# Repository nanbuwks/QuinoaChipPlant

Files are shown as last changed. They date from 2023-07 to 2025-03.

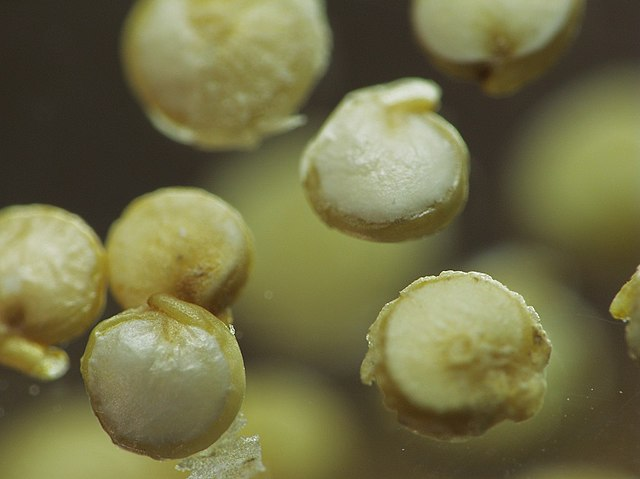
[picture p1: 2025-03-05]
images/2023-03-23-17-26-28.png

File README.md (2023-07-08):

# QuinoaChipPlant

キヌアの育種のために、撒種→結実を速いサイクルで回すためのプラントです。

## キヌアとは

キヌア（ Quinua ):南米で食されている雑穀。
栄養的に優れていて、スーパーフードとして注目されている。
乾燥/湿地、低温、塩地などの他の作物が育たない環境でも栽培ができる。
遺伝子が多様で、品種改良が期待される。

## このプラントの目的

1つのチップに1粒ずつ撒種し、水耕栽培を行います。
1つのラックにチップが24収納できますが、チップ1つ分はセンサーのために使うので1つのラックで23粒を撒きます。
芽が出たら1つのラックに10程度に間引きします。
100ラックで実験するとなると、1000株を育成することになります。
収量を目的とするのではなく、促成で種を回収することを目的としています。

# 育成ロボット

水換え、光照射、センサ接続ができるロボットボードです。
1000株分を育成するのは水替えも大変なので、自動で水換えを行います。
プログラムで自動運転できるので、一時冠水を繰り返すような運転を行うことができます。

## 組み立て方、使い方

「キヌア栽培のための制御回路をつくってみよう」
https://qiita.com/nanbuwks/items/138a8bbda59f0657b9df

## 開発コミュニティ

discord OpenHardTerrace 中の #chipplant で開発しています。
https://discord.gg/T8mKzFyu6m

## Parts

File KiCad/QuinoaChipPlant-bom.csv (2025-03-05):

ID | 指定子 | フットプリント | 数量 | 名称 | 供給業者、参考資料
1 | U2,U8,U6,U3,U4 | SparkFun_TB6612FNG_MOTOR_DRIVER_MODULE | 5 | SparkFun_TB6612FNG_MOTOR_DRIVER_MODULE
2 | J11 | JST_XH_B4B-XH-AM_1x04_P2.50mm_Vertical | 1 | LEVEL2
3 | J7,J10,J16,J9,J15,J8 | JST_XH_B2B-XH-AM_1x02_P2.50mm_Vertical | 6 | BULB
4 | D1,D4,D18,D3,D5,D7,D2,D11,D6,D10 | D_SOD-123 | 10 | D
5 | R10,R8,R9,R7 | R_1206_3216Metric_Pad1.30x1.75mm_HandSolder | 4 | 10K
6 | R16,R6,R15,R13,R14,R3,R17,R4,R12,R11,R5,R19,R20,R18 | R_1206_3216Metric_Pad1.30x1.75mm_HandSolder | 14 | 470
7 | ,,,,,,, |  | 8
8 | U5 | Seeedstudio_Grove_110990030_Vertical_4pin_2mmpitch | 1 | SEEED_GROVE
9 | J6,J5 | JST_XH_B2B-XH-AM_1x02_P2.50mm_Vertical | 2 | MOTOR
10 | D8,D9,D16,D15,D17,D14,D20,D13,D19,D12 | LED_D3.0mm | 10 | LED
11 | J4,J20 | TerminalBlock_Phoenix_PT-1,5-4-5.0-H_1x04_P5.00mm_Horizontal | 2 | Screw_Terminal_01x04
12 | U9 | YRB_YMD-10WR3_YRA_YMD-10WR3 | 1 | ~
13 | C5 | C_1206_3216Metric_Pad1.33x1.80mm_HandSolder | 1 | 0.1uF
14 | BZ1 | Buzzer_12x9.5RM7.6 | 1 | Buzzer
15 | C7,C9,C8,C14,C6,C16,C17,C10,C11,C12,C13 | R_1206_3216Metric_Pad1.30x1.75mm_HandSolder | 11 | C
16 | C3,C1 | C_1206_3216Metric_Pad1.33x1.80mm_HandSolder | 2 | C
17 | J13 | JST_XH_B4B-XH-AM_1x04_P2.50mm_Vertical | 1 | LEVEL4
18 | U1 | ESP32_DEVKIT_V1 | 1 | ESP32_DEVKIT_V1
19 | J3 | JST_XH_B4B-XH-AM_1x04_P2.50mm_Vertical | 1 | LEVEL1
20 | C2,C4,C15 | CP_Radial_D10.0mm_P2.50mm_P5.00mm | 3 | C_Polarized
21 | J18,J1 | JST_PH_B4B-PH-K_1x04_P2.00mm_Vertical | 2 | GROVE
22 | J2 | DCJACK | 1 | DCJACK
23 | TH1 | TerminalBlock_Phoenix_MKDS-1,5-2_1x02_P5.00mm_Horizontal | 1 | Thermistor
24 | J14 | DCJACK | 1 | DCJACK OPTIONAL
25 | U7 | TFT3.2_ILI9341 | 1 | CR2013-MI2120
26 | SW1 | SW_PUSH_6mm | 1 | SW_Push
27 | J12 | JST_XH_B4B-XH-AM_1x04_P2.50mm_Vertical | 1 | LEVEL3
28 | R1 | R_1206_3216Metric_Pad1.30x1.75mm_HandSolder | 1 | R
29 | JP3 | SolderJumper-2_P1.3mm_Bridged_Pad1.0x1.5mm | 1 | SolderJumper_2_Bridged

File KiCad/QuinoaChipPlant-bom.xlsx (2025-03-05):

Comment | Designator | Footprint | JLCPCB Part #（optional）
SparkFun_TB6612FNG_MOTOR_DRIVER_MODULE | U2,U8,U6,U3,U4,U12,U18,U16,U13,U14 | SparkFun_TB6612FNG_MOTOR_DRIVER_MODULE | C718237
LEVEL2 | J11 | LEVEL2 | C144395
BULB | J7,J10,J16,J9,J15,J8 | BULB | C158012
D | D1,D4,D18,D3,D5,D7,D2,D11,D6,D10 | D | C397619
10K | R10,R8,R9,R7 | 10K | C17902
470 | R16,R6,R15,R13,R14,R3,R17,R4,R12,R11,R5,R19,R20,R18 | 470 | C17936
SEEED_GROVE | U5 | SEEED_GROVE | C146064
MOTOR | J6,J5 | MOTOR | C158012
LED | D8,D9,D16,D15,D17,D14,D20,D13,D19,D12 | LED | C779429
Screw_Terminal_01x04 | J104,J120,J114,J130 | Screw_Terminal_01x02x02 | C8404
0.1uF | C5 | 0.1uF | C24497
Buzzer | BZ1 | Buzzer | C96222
C | C7,C9,C8,C14,C6,C16,C17,C10,C11,C12,C13 | C | C24497
C | C3,C1 | C | C24497
LEVEL4 | J13 | LEVEL4 | C144395
ESP32_DEVKIT_V1 | U1,U11 | ESP32_DEVKIT_V1 | C2897378
LEVEL1 | J3 | LEVEL1 | C144395
DCJACK | J2 | DCJACK | C16214
Thermistor | TH1 | Thermistor | C8404
CR2013-MI2120 | U7 | CR2013-MI2120 | C2897377
SW_Push | SW1 | SW_Push | C455098
LEVEL3 | J12 | LEVEL3 | C144395
R | R1 | R | C17902

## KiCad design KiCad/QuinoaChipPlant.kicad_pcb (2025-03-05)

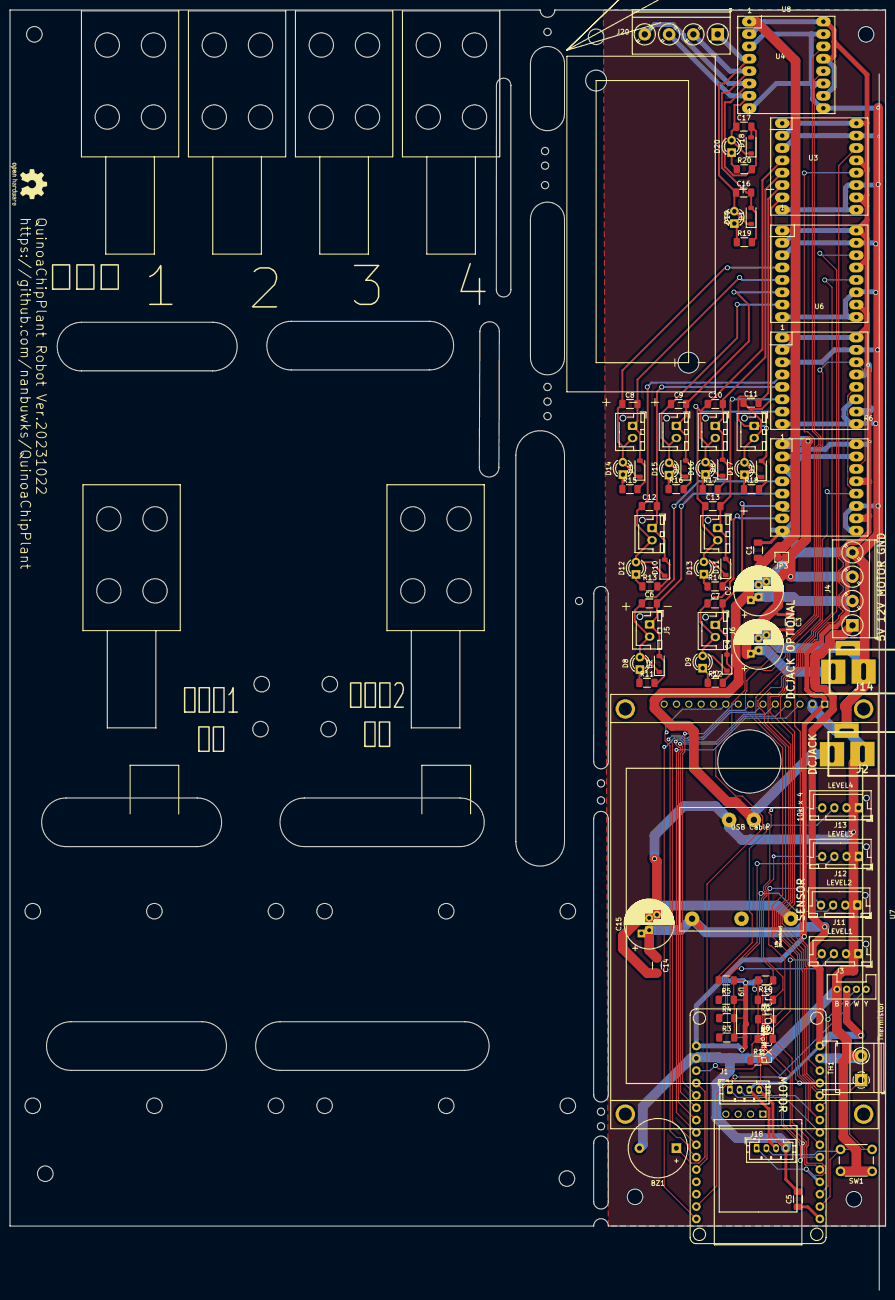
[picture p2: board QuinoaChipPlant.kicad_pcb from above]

Board: 2 copper layers, 180.0 x 263.2 mm, 138 parts (0 on the bottom side), 63 nets.

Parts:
BZ1: Buzzer; Buzzer_12x9.5RM7.6
C1, C3: C; C_1206_3216Metric_Pad1.33x1.80mm_HandSolder
C2, C4, C15: C_Polarized; CP_Radial_D10.0mm_P2.50mm_P5.00mm
C5: 0.1uF; C_1206_3216Metric_Pad1.33x1.80mm_HandSolder
C6, C7, C8, C9, C10, C11, C12, C13, C14, C16, C17: C; R_1206_3216Metric_Pad1.30x1.75mm_HandSolder
D1, D2, D3, D4, D5, D6, D7, D10, D11, D18: D; D_SOD-123
D8, D9, D12, D13, D14, D15, D16, D17, D19, D20: LED; LED_D3.0mm
J1, J18: GROVE; JST_PH_B4B-PH-K_1x04_P2.00mm_Vertical
J2: DCJACK
J3: LEVEL1; JST_XH_B4B-XH-AM_1x04_P2.50mm_Vertical
J4, J20: Screw_Terminal_01x04; TerminalBlock_Phoenix_PT-1,5-4-5.0-H_1x04_P5.00mm_Horizontal
J5, J6: MOTOR; JST_XH_B2B-XH-AM_1x02_P2.50mm_Vertical
J7, J8, J9, J10, J15, J16: BULB; JST_XH_B2B-XH-AM_1x02_P2.50mm_Vertical
J11: LEVEL2; JST_XH_B4B-XH-AM_1x04_P2.50mm_Vertical
J12: LEVEL3; JST_XH_B4B-XH-AM_1x04_P2.50mm_Vertical
J13: LEVEL4; JST_XH_B4B-XH-AM_1x04_P2.50mm_Vertical
J14: DCJACK OPTIONAL; DCJACK
JP3: SolderJumper_2_Bridged; SolderJumper-2_P1.3mm_Bridged_Pad1.0x1.5mm
R1: R; R_1206_3216Metric_Pad1.30x1.75mm_HandSolder
R3, R4, R5, R6, R11, R12, R13, R14, R15, R16, R17, R18, R19, R20: 470; R_1206_3216Metric_Pad1.30x1.75mm_HandSolder
R7, R8, R9, R10: 10K; R_1206_3216Metric_Pad1.30x1.75mm_HandSolder
REF07, REF09: MountingHole_4.3mm_M4_DIN965
REF08, REF08#2, REF10, REF11, REF12, REF12#2, REF12#3, REF13, REF14, REF15, REF16, REF17, REF18, REF19, REF21, REF22, REF23, REF24, REF26, REF27, REF100, REF111, REF112, REF113, REF114, REF115, REF116, REF117, REF119, REF120, REF121, REF122, REF123, REF124, REF125, REF126, REF127, REF128, REF129, REF130, REF131, REF132, REF133, REF134, REF140, REF141, REF230: MountingHole_3.2mm_M3
REF118: OSHW-Logo2_9.8x8mm_SilkScreen
SW1: SW_Push; SW_PUSH_6mm
TH1: Thermistor; TerminalBlock_Phoenix_MKDS-1,5-2_1x02_P5.00mm_Horizontal
U1: ESP32_DEVKIT_V1
U2, U3, U4, U6, U8: SparkFun_TB6612FNG_MOTOR_DRIVER_MODULE
U5: SEEED_GROVE; Seeedstudio_Grove_110990030_Vertical_4pin_2mmpitch
U7: CR2013-MI2120; TFT3.2_ILI9341
U9: YRB_YMD-10WR3_YRA_YMD-10WR3
USB Cable: MountingHole_8.4mm_M8

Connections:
+3V3: R1.1, R3.2, R4.2, R5.2, R6.2, R7.1, R8.2, R9.2, R10.2, U1.16 (3V3), U2.2 (VCC), U2.10 (PWMB), U2.13 (STBY), U2.16 (PWMA), U3.2 (VCC), U3.10 (PWMB), U3.13 (STBY), U3.16 (PWMA), U4.2 (VCC), U4.10 (PWMB), U4.13 (STBY), U4.16 (PWMA), U6.2 (VCC), U6.10 (PWMB), U6.13 (STBY), U6.16 (PWMA), U7.1 (VCC), U8.2 (VCC), U8.10 (PWMB), U8.13 (STBY), U8.16 (PWMA)
+5V: C14.1, C15.1, J1.3, J4.1, J18.3, U1.15 (VIN), U5.3 (Red/VCC), U9.3 (+Vo)
+12V: C1.1, C2.1, J2.1, J4.2, JP3.2 (B), U3.1 (VM), U4.1 (VM), U6.1 (VM), U8.1 (VM), U9.1 (-Vin)
+12VA: C3.1, C4.1, J4.3, J14.1, JP3.1 (A), U2.1 (VM)
BULB1: U1.10 (27), U3.14 (AI1)
BULB2: U1.11 (14), U3.12 (BI1)
BULB3: U1.13, U4.14 (AI1)
BULB4: U1.26 (21), U4.12 (BI1)
GND: BZ1.2 (+), C1.2, C2.2, C3.2, C4.2, C5.2, C14.2, C15.2, J1.4, J2.2, J2.3, J3.1, J3.2, J4.4, J11.1, J11.2, J12.1, J12.2, J13.1, J13.2, J14.2, J14.3, J18.4, SW1.1, TH1.2, U1.14 (GND), U1.17 (GND), U2.3 (GND), U2.8 (GND), U2.9 (GND), U2.11 (BI2), U2.15 (AI2), U3.3 (GND), U3.8 (GND), U3.9 (GND), U3.11 (BI2), U3.15 (AI2), U4.3 (GND), U4.8 (GND), U4.9 (GND), U4.11 (BI2), U4.15 (AI2), U5.4 (Black/GND), U6.3 (GND), U6.8 (GND), U6.9 (GND), U6.11 (BI2), U6.15 (AI2), U7.2 (GND), U8.3 (GND), U8.8 (GND), U8.9 (GND), U8.11 (BI2), U8.15 (AI2), U9.2 (+Vin), U9.5 (0V/-Vo)
GROVE1: U1.29 (22), U5.1 (Yellow/Dn/An/RX/SCL)
GROVE2: U1.3 (VN), U5.2 (White/Dn1/An1/TX/SDA)
MOTOR1: J1.1, U1.8 (25), U2.14 (AI1), U6.14 (AI1)
MOTOR2: J1.2, U1.9 (26), U2.12 (BI1), U6.12 (BI1)
unnamed: BZ1.1 (-), U1.19 (2)
unnamed: C16.2, D1.2 (A), J20.2, R19.2, U8.5 (A02)
unnamed: C16.1, D1.1 (K), D19.2 (A), J20.1, U8.4 (A01)
unnamed: C6.2, D2.2 (A), J5.1, R11.2, U2.5 (A02)
unnamed: C6.1, D2.1 (K), D8.2 (A), J5.2, U2.4 (A01)
unnamed: C7.2, D3.2 (A), J6.1, R12.2, U2.6 (B02)
unnamed: C7.1, D3.1 (K), D9.2 (A), J6.2, U2.7 (B01)
unnamed: C8.2, D4.2 (A), J9.1, R15.2, U3.5 (A02)
unnamed: C9.2, D5.2 (A), J10.1, R16.2, U3.6 (B02)
unnamed: C10.2, D6.2 (A), J15.1, R17.2, U4.5 (A02)
unnamed: C11.2, D7.2 (A), J16.1, R18.2, U4.6 (B02)
unnamed: D8.1 (K), R11.1
unnamed: D9.1 (K), R12.1
unnamed: C12.2, D10.2 (A), J7.1, R13.2, U6.5 (A02)
unnamed: C12.1, D10.1 (K), D12.2 (A), J7.2, U6.4 (A01)
unnamed: C13.2, D11.2 (A), J8.1, R14.2, U6.6 (B02)
unnamed: C13.1, D11.1 (K), D13.2 (A), J8.2, U6.7 (B01)
unnamed: D12.1 (K), R13.1
unnamed: D13.1 (K), R14.1
unnamed: C8.1, D4.1 (K), D14.2 (A), J9.2, U3.4 (A01)
unnamed: D14.1 (K), R15.1
unnamed: C9.1, D5.1 (K), D15.2 (A), J10.2, U3.7 (B01)
unnamed: D15.1 (K), R16.1
unnamed: C10.1, D6.1 (K), D16.2 (A), J15.2, U4.4 (A01)
unnamed: D16.1 (K), R17.1
unnamed: C11.1, D7.1 (K), D17.2 (A), J16.2, U4.7 (B01)
unnamed: D17.1 (K), R18.1
unnamed: C17.2, D18.2 (A), J20.4, R20.2, U8.6 (B02)
unnamed: C17.1, D18.1 (K), D20.2 (A), J20.3, U8.7 (B01)
unnamed: D19.1 (K), R19.1
unnamed: D20.1 (K), R20.1
unnamed: J3.3, R3.1
unnamed: J11.3, R4.1
unnamed: J12.3, R5.1
unnamed: J13.3, R6.1
unnamed: U1.20 (4), U7.8 (LED)
unnamed: U1.23 (5), U7.3 (~CS)
unnamed: U1.21 (16), U7.4 (RESET)
unnamed: U1.22 (17), U7.5 (D/~C)
unnamed: U1.24 (18), U7.7 (SCK)
unnamed: U1.25 (19), U7.9 (MISO)
unnamed: U1.30 (23), U7.6 (MOSI)
unnamed: C5.1, U1.1 (EN)
RELAY1: U1.12, U8.14 (AI1)
RELAY2: U1.7 (33), U8.12 (BI1)
SW_THERMISTOR: J18.2, R1.2, SW1.2, TH1.1, U1.2 (VP)
WATERSENSOR1: J3.4, J18.1, R7.2, U1.4 (34)
WATERSENSOR2: J11.4, R8.1, U1.5 (35)
WATERSENSOR3: J12.4, R9.1, U1.6 (32)
WATERSENSOR4: J13.4, R10.1, U1.18 (15)

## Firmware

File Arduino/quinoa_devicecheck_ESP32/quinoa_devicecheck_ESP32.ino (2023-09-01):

/* Version 202304
#define PUMP0_PIN 27
#define PUMP1_PIN 26
#define FAN_PIN 22
#define BEEP_PIN 2
#define WATERSENSOR_PIN 25
#define BEEP
*/


/* Version 202304 */
#define PUMP0_PIN 25
#define PUMP1_PIN 26
#define VALVE0_PIN 27
#define VALVE1_PIN 14
#define VALVE2_PIN 13
#define VALVE3_PIN 21
#define GROVE0_PIN 22
#define GROVE1_PIN 39         // VN input only
#define BEEP_PIN 2
#define WATERSENSOR0_PIN 34
#define WATERSENSOR1_PIN 35
#define WATERSENSOR2_PIN 32
#define WATERSENSOR3_PIN 33   
#define BEEP
#define SW_THERMISTOR_PIN A0  // VP input only
\
//------------------------------------------------------------------------------
void setup() {

  Serial.begin(115200);
  delay(100);
  Serial.println("WATERCONTROLLER START");
  pinMode(WATERSENSOR0_PIN, INPUT);
  pinMode(WATERSENSOR1_PIN, INPUT);
  pinMode(WATERSENSOR2_PIN, INPUT);
  pinMode(WATERSENSOR3_PIN, INPUT);
  pinMode(PUMP0_PIN, OUTPUT);
  pinMode(PUMP1_PIN, OUTPUT);
  pinMode(BEEP_PIN, OUTPUT);
  pinMode(VALVE0_PIN, OUTPUT);
  pinMode(VALVE1_PIN, OUTPUT);
  pinMode(VALVE2_PIN, OUTPUT);
  pinMode(VALVE3_PIN, OUTPUT);
  digitalWrite(PUMP0_PIN, 0);
  digitalWrite(PUMP1_PIN, 0);
  digitalWrite(BEEP_PIN, 0);
  digitalWrite(VALVE0_PIN, 0);
  digitalWrite(VALVE1_PIN, 0);
  digitalWrite(VALVE2_PIN, 0);
  digitalWrite(VALVE3_PIN, 0);

  
}

void loop()
{
 
  Serial.printf("WATERSENSOR0:%d\n",digitalRead(WATERSENSOR0_PIN ));
  Serial.printf("WATERSENSOR1:%d\n",digitalRead(WATERSENSOR1_PIN ));
  Serial.printf("WATERSENSOR2:%d\n",digitalRead(WATERSENSOR2_PIN ));
  Serial.printf("WATERSENSOR3:%d\n",digitalRead(WATERSENSOR3_PIN ));
  Serial.printf("BEEP\n");
  digitalWrite(BEEP_PIN, 1);
  delay(1000);
  digitalWrite(BEEP_PIN, 0);
  delay(1000);
  Serial.printf("PUMP0\n");
  digitalWrite(PUMP0_PIN, 1);
  delay(1000);
  digitalWrite(PUMP0_PIN, 0);
  delay(1000);
  Serial.printf("PUMP1\n");
  digitalWrite(PUMP1_PIN, 1);
  delay(1000);
  digitalWrite(PUMP1_PIN, 0);
  delay(1000);
  Serial.printf("VALVE0\n");
  digitalWrite(VALVE0_PIN, 1);
  delay(1000);
  digitalWrite(VALVE0_PIN, 0);
  delay(1000);
  Serial.printf("VALVE1\n");
  digitalWrite(VALVE1_PIN, 1);
  delay(1000);
  digitalWrite(VALVE1_PIN, 0);
  delay(1000);
  Serial.printf("VALVE2\n");
  digitalWrite(VALVE2_PIN, 1);
  delay(1000);
  digitalWrite(VALVE2_PIN, 0);
  delay(1000);
  Serial.printf("VALVE3\n");
  digitalWrite(VALVE3_PIN, 1);
  delay(1000);
  digitalWrite(VALVE3_PIN, 0);
  delay(1000);
  
  
  
}     

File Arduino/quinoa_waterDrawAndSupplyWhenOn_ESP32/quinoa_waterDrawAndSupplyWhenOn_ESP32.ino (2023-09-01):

/* Version 202304
#define PUMP0_PIN 27
#define PUMP1_PIN 26
#define FAN_PIN 22
#define BEEP_PIN 2
#define WATERSENSOR_PIN 25
#define BEEP
*/


/* Version 202304 */
#define PUMP0_PIN 25
#define PUMP1_PIN 26
#define BULB0_PIN 27
#define BULB1_PIN 14
#define BULB2_PIN 13
#define BULB3_PIN 21
#define GROVE0_PIN 22
#define GROVE1_PIN 39         // VN input only
#define BEEP_PIN 2
#define WATERSENSOR0_PIN 34
#define WATERSENSOR0_PIN 35
#define WATERSENSOR0_PIN 32
#define WATERSENSOR0_PIN 33   
#define BEEP
#define SW_THERMISTOR_PIN A0  // VP input only

void beep(int millis) {
  Serial.printf("beep:%d", millis);
#ifdef BEEP
  digitalWrite(BEEP_PIN, HIGH);
#endif
  delay(millis);
  digitalWrite(BEEP_PIN, LOW);
}
void pi() {
  beep(200);
}
void pipi() {
  beep(200);
  delay(50);
  beep(100);

}
void pipipipi() {
  beep(200);
  delay(50);
  beep(100);
  delay(100);
  beep(100);
  delay(100);
  beep(100);

}
void peee() {
  beep(1000);
}


void runPUMP0() {
  digitalWrite(PUMP0_PIN, HIGH);
}
void stopPUMP0() {
  digitalWrite(PUMP0_PIN, LOW);
}
//------------------------------------------------------------------------------
void setup() {

  Serial.begin(115200);
  delay(100);
  Serial.println("WATERCONTROLLER START");
  pinMode(WATERSENSOR_PIN, INPUT_PULLUP);
  pinMode(PUMP0_PIN, OUTPUT);
  pinMode(PUMP1_PIN, OUTPUT);
  pinMode(BEEP_PIN, OUTPUT);
  digitalWrite(PUMP0_PIN, 0);
  digitalWrite(PUMP1_PIN, 0);
  digitalWrite(FAN_PIN, 0);
  digitalWrite(BEEP_PIN, 0);
  pipi();
  Serial.println( digitalRead(WATERSENSOR_PIN));
  // 5分排水
  Serial.println("排水");
  digitalWrite(PUMP0_PIN, 1);
  delay(300000);
  digitalWrite(PUMP0_PIN, 0);

  
}

void loop()
{
    // 給水
  while ( 1 == digitalRead(WATERSENSOR_PIN )){
    Serial.println("給水");
    digitalWrite(PUMP1_PIN, 1);
    while ( 1 == digitalRead(WATERSENSOR_PIN )){
      delay(1000);
  }}
  while ( 0 == digitalRead(WATERSENSOR_PIN )){
    Serial.println("完了");
    digitalWrite(PUMP1_PIN, 0);
    while ( 0 == digitalRead(WATERSENSOR_PIN )){
      delay(1000);
  }}
  delay(1000);
}     

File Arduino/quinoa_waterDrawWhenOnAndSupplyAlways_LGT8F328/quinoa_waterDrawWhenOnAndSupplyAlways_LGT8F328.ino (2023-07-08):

#define PUMP0_PIN 8  // 給水用
#define PUMP1_PIN 11 // 排水用
#define SW_THERMISTOR_PIN A4
#define BEEP_PIN 15
#define WATERSENSOR_PIN 19
#define BEEP

void beep(int millis) {
  Serial.print("beep:"+ millis);
#ifdef BEEP
  digitalWrite(BEEP_PIN, HIGH);
#endif
  delay(millis);
  digitalWrite(BEEP_PIN, LOW);
}
void pi() {
  beep(200);
}
void pipi() {
  beep(200);
  delay(50);
  beep(100);

}
void pipipipi() {
  beep(200);
  delay(50);
  beep(100);
  delay(100);
  beep(100);
  delay(100);
  beep(100);

}
void peee() {
  beep(1000);
}


void runPUMP0() {
  digitalWrite(PUMP0_PIN, HIGH);
}
void stopPUMP0() {
  digitalWrite(PUMP0_PIN, LOW);
}

void flush(int flushtime){
  
  Serial.println("排水");
  digitalWrite(PUMP1_PIN, 0);
  delay(flushtime);
  digitalWrite(PUMP1_PIN, 1);
  
  
}
//------------------------------------------------------------------------------
void setup() {

  Serial.begin(115200);
  delay(100);
  Serial.println("WATERCONTROLLER START");
  pinMode(WATERSENSOR_PIN, INPUT_PULLUP);
  pinMode(PUMP0_PIN, OUTPUT);
  pinMode(PUMP1_PIN, OUTPUT);
  pinMode(BEEP_PIN, OUTPUT);
  digitalWrite(PUMP1_PIN, 1);
  digitalWrite(PUMP0_PIN, 0);
  digitalWrite(SW_THERMISTOR_PIN, 0);
  digitalWrite(BEEP_PIN, 0);
  pipi();
  Serial.println( digitalRead(WATERSENSOR_PIN));
  // 5分排水
  flush(3000);

  
}

void dummy()
{

  Serial.println("給水");
  digitalWrite(PUMP0_PIN, 1);
  delay(60000);
  digitalWrite(PUMP0_PIN, 0);
/*
  Serial.println("排水");
  digitalWrite(PUMP1_PIN, 0);
  delay(3000);
  digitalWrite(PUMP1_PIN, 1);
*/
}
void loop(){
  
    // 給水
  while ( 1 == digitalRead(WATERSENSOR_PIN )){   // 水位が充たされてなければこのループを回る
    Serial.println("給水");
    digitalWrite(PUMP0_PIN, 1);
    while ( 1 == digitalRead(WATERSENSOR_PIN )){ // 水位が充たされるまでこのループを回る
      delay(100);
  }}
  while ( 0 == digitalRead(WATERSENSOR_PIN )){
    Serial.println("完了");
    digitalWrite(PUMP0_PIN, 0);
    while ( 0 == digitalRead(WATERSENSOR_PIN )){  // 水位が充たされていたらこのループを回る
      delay(100);
      int check = analogRead(SW_THERMISTOR_PIN);  // ボタンが押されたら
      if (0 == check) flush(3000);                // 一定時間排水
  
  }}
  delay(100);
}     

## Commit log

2023-05-08 mv KiCad file from IoTHandyFan
    [handyfan-B_Cu.gbr, handyfan-B_Mask.gbr, handyfan-B_Paste.gbr, handyfan-B_SilkS.gbr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]
2023-05-08 changename KiCad files.
    [QuinoaChipPlant.kicad_pcb, QuinoaChipPlant.sch, handyfan.csv]
2023-05-08 change to KiCad 7 files from KiCad 5 files.
    [QuinoaChipPlant.kicad_pcb, QuinoaChipPlant.kicad_sch, QuinoaChipPlant.sch]
2023-05-10 make pump, bulb , sensor PCB.
    [QuinoaChipPlant.kicad_pcb, QuinoaChipPlant.kicad_sch]
2023-05-10 PCB release 20230510 Version.
    [QuinoaChipPlant-B_Cu.gbr, QuinoaChipPlant-B_Mask.gbr, QuinoaChipPlant-B_Paste.gbr, QuinoaChipPlant-B_Silkscreen.gbr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]
2023-05-21 Add esp32 sketchc
2023-07-08 modify arduino sketch
2023-09-01 202305 version
    [QuinoaChipPlant-B_Cu.gbr, QuinoaChipPlant-B_Mask.gbr, QuinoaChipPlant-B_Paste.gbr, QuinoaChipPlant-B_Silkscreen.gbr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]
2023-09-01 add devicecheck program
2025-03-05 202311 version
    [QuinoaChipPlant-B_Cu.gbr, QuinoaChipPlant-B_Mask.gbr, QuinoaChipPlant-B_Paste.gbr, QuinoaChipPlant-B_Silkscreen.gbr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]
